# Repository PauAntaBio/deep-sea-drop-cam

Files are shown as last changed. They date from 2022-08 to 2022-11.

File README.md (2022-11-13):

# deep-sea-drop-cam
Blue Eye: a low cost Arduino-powered device to explore the deep sea up to 500 meters of depth at a cost of US$1,400.



In 2018, I attended All Hands on Deck, an event co-organized by the MIT Media Lab and NOAA Office of Ocean Exploration and Research, in which policy makers, scientists, activists and change makers in ocean exploration met to imagine new ways to empower an open, inclusive global community of ocean explorers.

This event motivated me to develop a low cost device to explore the deep sea, after I learned that "70 percent of countries have deep-sea environments within their maritime Exclusive Economic Zones (EEZs), yet only 16 percent of them are able to explore those environments. The scarcity of technological capability and knowledge leads to a lack of exploration, inappropriate or inadequate management decisions, and unaware populations" (source: MIT Media Lab My Deep Sea, My Backyard).

Acknowledgements

Special thanks to Brennan Phillips PhD, Assistant Professor of Ocean Engineering at the University of Rhode Island, for sharing his knowledge, passion and enthusiasm with me. His advice was key for building the Blue Eye (he knows everything, but if he doesn't know, he knows who does!).

Many thanks to Cristobal Huguet for taking me to test the Blue Eye in the marine reserve and to Maria Cefalí PhD and Juancho Movilla PhD (Research Station "Jaume Ferrer" in Menorca, Spain) for their feedback and recommendations.

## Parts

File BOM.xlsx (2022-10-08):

Bill of Materials (BOM)
Note: some prices from 2019 and some from 2022
Items in green are optional
item | distributor | name | units | $ per unit | item cost | subtotals
POWER |  |  |  |  |  | $47.13
Battery for lights and burn-wire (https://www.amazon.com/gp/product/B07VLR5ZW9/ref=ppx_yo_dt_b_search_asin_title?ie=UTF8&psc=1) | Amazon | 3S Lipo Battery - Energy tech RC Battery 11.1V 30C 3000mAh with Deans-T Plug for RC Car Airplane Helicopter FPV Boat Drone | 1 | $21.99 | $21.99
T-plug connector for battery (https://www.amazon.com/gp/product/B07FSPTPWL/ref=ppx_yo_dt_b_asin_title_o01_s00?ie=UTF8&psc=1) | Amazon | OliYin 3pcs Male Deans T-Plug to Male JST Connector Adapter 3.93inch Heavy Duty 20awg Wire(Pack of 3) | 1 | $8.69 | $8.69
Connector cable (https://www.adafruit.com/product/261) | Adafruit | JST PH 2-Pin Cable - Female Connector 100mm | 2 | $0.75 | $1.50
Battery for motherboard (https://www.adafruit.com/product/328) | Adafruit | Lithium Ion Polymer Battery - 3.7v 2500mAh | 1 | $14.95 | $14.95
CAMERA |  |  |  |  |  | $199.89
GoPro Session Hero 5 (https://www.walmart.com/ip/GoPro-HERO-Session-Waterproof-HD-Action-Camera/49933596?athcpid=49933596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) | GoPro | GoPro HERO Session Waterproof HD Action Camera | 1 | $199.89 | $199.89 |  | cost from 2016
MOTHERBOARD |  |  |  |  |  | $224.46
Microcontroller (https://store.arduino.cc/usa/mkr-wifi-1010) | Arduino | Arduino MKR WiFi 1010 | 1 | $33.90 | $33.90
Memory Shield (https://store.arduino.cc/usa/mkr-mem-shield) | Arduino | ARDUINO MKR MEM SHIELD | 1 | $22.90 | $22.90 |  | optional: needed if you want to have a log
microSD card (https://www.amazon.com/Sandisk-Ultra-Micro-UHS-I-Adapter/dp/B073K14CVB) | Amazon | SanDisk 16GB Ultra microSDHC UHS-I Memory Card with Adapter - 98MB/s, C10, U1, Full HD, A1, Micro SD Card - SDSQUAR-016G-GN6MA | 1 | $5.79 | $5.79 |  | optional: needed if you want to have a log
Relay (https://www.seeedstudio.com/Grove-Relay.html) | Seeed Studio | Grove Relay, operate voltage: 3.3V-5V (SKU 103020005) | 1 | $3.20 | $3.20
PCB breadboard (https://www.adafruit.com/product/589) | Adafruit | Adafruit Perma-Proto Quarter-sized Breadboard PCB x 3 units | 1 | $8.50 | $8.50
External switch (https://bluerobotics.com/store/comm-control-power/switch/switch-10-5a-r1/) | Blue Robotics | Power switch | 1 | $14.00 | $14.00
Magnetic switch (https://www.amazon.com/gp/product/B0009SUF08) | Amazon | Magnetic switch | 1 | $6.48 | $6.48
Half sized breadboard (https://www.adafruit.com/product/64) | Adafruit | Half sized breadboard | 1 | $5.00 | $5.00
Temperature and humidity sensor (https://www.adafruit.com/product/393) | Adafruit | AM2302 (wired DHT22) temperature-humidity sensor | 1 | $15.00 | $15.00 |  | optional: needed if you want to measure temperature and humidity inside the device
Resistors | Adafruit | 220 Ohm resistors (Pack 25) | 1 | $0.75 | $0.75
LEDs (https://www.adafruit.com/product/4203) | Adafruit | Diffused 5mm LED Pack - 5 LEDs each in 5 Colors (Pack 25) | 1 | $2.95 | $2.95
Solid wires (https://www.amazon.com/gp/product/B07TX6BX47/ref=ppx_yo_dt_b_search_asin_title?ie=UTF8&psc=1) | Amazon | Solid Wire-Solid Wire Kit-6 Different Colored 30 Feet spools 22 Gauge Jumper Wire- Hook up Wire Kit | 1 | $14.99 | $14.99
Wire connectors | Amazon | WAGO 221 Lever-Nuts 75pc Wire Connector Assortment Pack with Case | 1 | $42.00 | $42.00
Electronics Tray (4" Series) (https://bluerobotics.com/store/watertight-enclosures/4-series/wte4-etray-r1/?wccp_component_selection%5B1549890504%5D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) | Blue Robotics | Electronics Tray (4" Series) | 1 | $49.00 | $49.00
LIGHTS |  |  |  |  |  | $198.00
Lumen Subsea Light (https://bluerobotics.com/store/thrusters/lights/lumen-r2-rp/) | Blue Robotics | Lumen Subsea Light 1500 lumens | 2 | $99.00 | $198.00
HOUSING |  |  |  |  |  | $352.00
Dome end cap (https://bluerobotics.com/store/watertight-enclosures/locking-series/wte-end-cap-vp/) | Blue Robotics | Dome end cap | 1 | $39.00 | $39.00
Flat end cap (https://bluerobotics.com/store/watertight-enclosures/locking-series/wte-end-cap-vp/) | Blue Robotics | Aluminium end cap with 5 holes | 1 | $20.00 | $20.00
Enclosure clamp (https://bluerobotics.com/store/watertight-enclosures/enclosure-clamp/) | Blue Robotics | Enclosure clamp | 1 | $39.00 | $39.00
O-Ring flange (https://bluerobotics.com/store/watertight-enclosures/locking-series/wte-flange-vp/) | Blue Robotics | O-Ring flange | 2 | $29.00 | $58.00
Aluminum tube (https://bluerobotics.com/store/uncategorized/wte4-m-tube-12-r3-rp/) | Blue Robotics | Aluminum tube 11.75" | 1 | $180.00 | $180.00
Pole clamp | Own design | Own design (see 3D parts folder) | 1 | $0.00 | $0.00
Lights mount | Own design | Own design (see 3D parts folder) | 2 | $0.00 | $0.00
Cable penetrator (https://bluerobotics.com/store/cables-connectors/penetrators/penetrator-vp/) | Blue Robotics | Cable penetrator for 6mm cable x 3 | 3 | $4.00 | $12.00
Cable penetrator blank (https://bluerobotics.com/store/cables-connectors/penetrators/penetrator-blank-vp/) | Blue Robotics | Cable penetrator for 6mm blank | 1 | $4.00 | $4.00
DROP AND RELEASE MECHANISM |  |  |  |  |  | $168.34
Carbon fiber tube (https://dragonplate.com/carbon-fiber-roll-wrapped-twill-tube-075-id-x-24-gloss-finish) | All Red | Carbon Tube .75" x .875" x 24" | 1 | $32.54 | $32.54
Top Modular Connector (https://dragonplate.com/075-Male-Clevis-Connector) | All Red | Modular Connector .75" Male Clevis Connector | 1 | $11.00 | $11.00
Bottom Modular Connector (https://dragonplate.com/075-short-threaded-end-connector) | All Red | Modular Connector .75" Short Threaded End Conn. (1/4-20) | 1 | $10.50 | $10.50
Link bottom Modular Connector (https://dragonplate.com/link-for-075-modular-connectors-3-hole) | All Red | Modular Connector .75" 3 Hole Link | 1 | $7.00 | $7.00
Epoxy adhesive (https://dragonplate.com/Double_Bubble-Orange-High-Peel-Strength-Epoxy-Adhesive) | All Red | Double/Bubble Orange High Peel Strength Epoxy Adhesive | 1 | $1.40 | $1.40
Bolts (https://dragonplate.com/Stainless-Steel-Black-Oxide-Bolt--075-x-1_4-20-thread) | All Red | Black Oxide SS 1/4-20x3/4 BHCS Black Oxide | 4 | $0.35 | $1.40
Ring terminals (https://www.mcmaster.com/catalog/125/817) | McMaster-Carr | Heat-Shrink Ring Terminals for 22-18 Wire Gauge and 1/4" Screw Size (pack of 10) | 1 | $7.54 | $7.54
loop to loop lanyard (https://www.mcmaster.com/catalog/125/1524) | McMaster-Carr | 18-8 Stainless Steel Lanyard - Not for Lifting, Loop-to-Loop, 1/16" Rope Diameter, 6" Long, Nylon | 1 | $2.80 | $2.80
Burnwire (https://www.amazon.com/gp/product/B07CHTY1VV/ref=ppx_yo_dt_b_asin_title_o02_s01?ie=UTF8&psc=1) | Amazon | Fast Fog 50 ft - 30 Gauge AWG Nichrome 80 Resistance Wire 50’ Length | 1 | $7.81 | $7.81
Biodegradable bags (https://www.amazon.com/gp/product/B07P6NN4RV/ref=ppx_yo_dt_b_asin_title_o02_s00?ie=UTF8&psc=1) | Amazon | 100% Organic Cotton, Biodegradable and Reusable Premium Quality Muslin Drawstring Bags,Size : 10x12 inches (Pack of 25) | 1 | $31.99 | $31.99
Biodegradable cord (https://www.amazon.com/Macrame-Cord-109Yards（328Feet-Natural-Cotton/dp/B09CNT9RZC) | Amazon | 3mm x 109Yards (328Feet), Natural Cotton Macrame Rope | 1 | $9.99 | $9.99
Nylon 3mm outdoor cord (https://www.amazon.com/TRIWONDER-Reflective-Paracord-Guyline-Packaging/dp/B07FKHDGC9) | Amazon | Reflective Nylon Paracord, Tent Guyline Rope for Camping Tent, Outdoor Packaging, 50 Feet Cord | 1 | $6.99 | $6.99
Weigth (https://www.amazon.com/Scuba-Choice-Coated-Diving-Weights/dp/B01M1RJ976) | Amazon | Scuba Choice Blue Vinyl Coated Diving Lead Weights, 2LB | 1 | $14.18 | $14.18
Deep water float |  | See picture in GitHub repository | 1 | $5.00 | $5.00
Galvanic release (https://www.lfsmarineoutdoor.com/Neptune-Galvanic-Time-Release?quantity=1&type=632) | LFS Marine outdoor | Neptune Galvanic Time Release 1 day | 10 | $1.82 | $18.20
ADDITIONAL COMPONENTS |  |  |  |  |  | $220.15
Vent plug (https://bluerobotics.com/store/cables-connectors/penetrators/vent-m-plug-10-a-r1/) | Blue Robotics | Vent plug | 1 | $4.00 | $4.00
Vacuum plug (https://bluerobotics.com/store/watertight-enclosures/enclosure-tools-supplies/vacuum-plug/) | Blue Robotics | Vacuum plug | 1 | $8.00 | $8.00
Vacuum pump (https://www.amazon.com/gp/product/B00KB9D3UO/ref=ppx_yo_dt_b_asin_title_o05_s00?ie=UTF8&psc=1) | Amazon | ABN Brake Bleeder Kit Universal Vacuum Pump & Brake Bleeding Tester Set for Automotive Service & Airtight Food Canning | 1 | $20.99 | $20.99
Silicone (https://bluerobotics.com/store/watertight-enclosures/enclosure-tools-supplies/tool-silicone-grease-10g-r1/) | Blue Robotics | Silicone grease 10g | 1 | $3.00 | $3.00
Potting kit (https://bluerobotics.com/store/cables-connectors/tools/tool-potting-kit-r1/) | Blue Robotics | Potting kit | 1 | $10.00 | $10.00
Acetone wipes (https://bluerobotics.com/store/cables-connectors/tools/potting-acetone-wipes-qty10-r1-rp/) | Blue Robotics | Acetone cable preparation wipes (10 pcs) | 1 | $4.00 | $4.00
Potting compound (https://bluerobotics.com/store/cables-connectors/tools/potting-thx-80a-r1/) | Blue Robotics | WetLink Thixotropic 80A Potting Compound (USA ONLY) | 1 | $19.00 | $19.00
Potting dispenser (https://bluerobotics.com/store/cables-connectors/tools/potting-dispenser-r1-rp/) | Blue Robotics | Potting cartridge dispenser | 1 | $23.00 | $23.00
Cable zip ties (https://www.amazon.com/HAVE-ME-TD-Cable-Ties/dp/B08TVLYB3Q) | Amazon | Cable Zip Ties,400 Pack Black Zip Ties Assorted Sizes 12+8+6+4 Inch | 1 | $6.59 | $6.59
Bait bag (https://www.lfsmarineoutdoor.com/Flexible-Bait-Bag-Material) | LFS Marine outdoor | Flexible Bait Bag Material | 1 | $0.25 | $0.25
Stainless Steel Screws and Nuts (https://www.amazon.com/gp/product/B071KBVZVV/ref=ppx_yo_dt_b_asin_title_o06_s00?ie=UTF8&psc=1) | Amazon | VIGRUE M2-M3-M4-1080PCS Stainless Steel Screws and Nuts, 1080 Pcs Hex Socket Head Cap, Silver | 1 | $25.99 | $25.99
Lipo battery storage (https://www.amazon.com/gp/product/B005HTH78W/ref=ppx_yo_dt_b_asin_title_o02_s00?ie=UTF8&psc=1) | Amazon | Aketek Silver Large Size Lipo Battery Guard Sleeve/Bag for Charge & Storage | 1 | $7.77 | $7.77
Velcro (https://www.amazon.com/VELCRO-Brand-Sticky-Fasteners-Perfect/dp/B00006IC2M?__mk_es_US=ÅMÅŽÕÑ) | Amazon | VELCRO Brand 5 Ft x 3/4 In | White Tape Roll with Adhesive | 1 | $8.00 | $8.00
Electric tape (https://www.amazon.com/Scotch-Heat-Resistant-Listed-Certified-Electrical/dp/B001AXD0EY) | Amazon | Scotch Vinyl Electrical Tape, Black, 3/4-in by 66-ft, 1-Roll | 1 | $2.06 | $2.06
VHB tape (https://www.amazon.com/Double-Mounting-Waterproof-Outdoor-Black，1/dp/B08T1HB5LJ) | Amazon | Double Sided Tape, 3M Heavy Duty Mounting Tape, Waterproof VHB Foam Tape | 1 | $9.00 | $9.00
USB for Arduino (https://www.amazon.com/AmazonBasics-Male-Micro-Cable-Black/dp/B0711PVX6Z?hvadid=198093101467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) | Amazon | AmazonBasics USB 2.0 A-Male to Micro B Charger Cable, 3 feet | 1 | $4.99 | $4.99
Battery charger (3S lipo) (https://www.amazon.com/Charger-Balance-Discharger-Digital-Batteries/dp/B07V5CPYRS) | Amazon | LiPo Charger RC Balance Fast Charger Discharger 1S-6S AC/DC B6V2 Digital Battery Pack Charger for NiCd Li-ion Life NiMH LiHV PB Smart Batteries | 1 | $46.57 | $46.57
Battery charger (micro-lipo) (https://www.adafruit.com/product/1904) | Adafruit | Adafruit Micro-Lipo Charger for LiPo/LiIon Batt w/MicroUSB Jack - v1 P | 1 | $6.95 | $6.95
Power supply cord (https://www.amazon.com/Pinfox-Universal-Appliance-Replacement-Pigtail/dp/B06XRKXLVV?s=hi) | Amazon | Pinfox 6ft 16 Gauge 3 Prong Heavy Duty Replacement Power Supply Cord Cable 110V 115V 120V Pigtail for Universal AC Appliance, NEMA 5-15 Plug US SJT 16AWG (12A) | 1 | $9.99 | $9.99
 |  |  |  | Total cost | $1409.97
TOOLS
Terminal Crimper Tool (https://www.amazon.com/gp/product/B0069TRKJ0/ref=ppx_yo_dt_b_asin_title_o03_s00?ie=UTF8&psc=1) | Amazon | Titan Tools 11477 Ratcheting Wire Terminal Crimper Tool | 1 | $18.95 | $18.95
Solder (https://www.amazon.com/ANBES-Soldering-Iron-Kit-Electronics/dp/B06XZ31W3M) | Amazon | ANBES Soldering Iron Kit Electronics, 60W Adjustable Temperature Welding Tool | 1 | $17.99 | $17.99
Solder wire (https://www.amazon.com/gp/product/B00AYJ0B7Y/ref=ppx_yo_dt_b_asin_title_o05_s00?ie=UTF8&psc=1) | Amazon | Kester 44 Rosin Core Solder 63/37 .020" 3/4oz Dispense-Pak | 1 | $11.89 | $11.89
Soldering tip (https://www.amazon.com/gp/product/B00762AGTA/ref=ppx_yo_dt_b_asin_title_o05_s00?ie=UTF8&psc=1) | Amazon | Hakko T18BL Series Soldering Tip for FX-888/FX-8801, Conical, R 0.2 mm x 22.5 mm | 1 | $9.46 | $9.46
Clip test leads (https://www.adafruit.com/product/1008) | Adafruit | Small Alligator Clip Test Lead (set of 12) | 1 | $3.95 | $3.95
Digital multimeter (https://www.amazon.com/Etekcity-Multimeter-MSR-R500-Electronic-Multimeters/dp/B01N9QW620) | Amazon | Etekcity Digital Multimeter, Amp Volt Ohm Voltage Tester Meter with Diode and Continuity Test, Dual Fused for Anti-Burn | 1 | $9.15 | $9.15
Wire strippers (https://www.amazon.com/VISE-GRIP-Stripping-Cutter-8-Inch-2078309/dp/B000JNNWQ2) | Amazon | IRWIN Vise-Grip Wire Stripping Tool / Wire Cutter, 8-Inch (2078309) | 1 | $14.00 | $14.00
Hex key set (https://www.amazon.com/30-Piece-Premium-Assortment-Vanadium-Chamfered/dp/B08GKHLJWR) | Amazon | Hex Key Allen Wrench Set | 1 | $12.99 | $12.99
Clamp on vise (https://www.amazon.com/MYTEC-Home-Vise-Clamp-3-0/dp/B07T5RL3DM) | Amazon | Clamp on vise | 1 | $27.87 | $27.87
Helping hands (https://www.amazon.com/Third-Soldering-Workshop-Non-Slip-Aluminum/dp/B079CHJQKH) | Amazon | Adjustable helping hands for soldering | 1 | $29.99 | $29.99

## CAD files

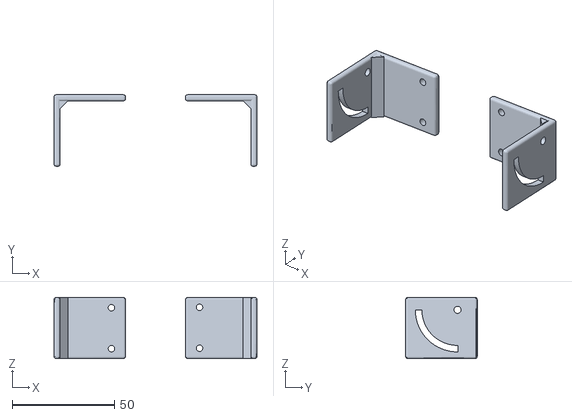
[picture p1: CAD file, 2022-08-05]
3D parts/light support.stl
99.3 x 35.0 x 30.0

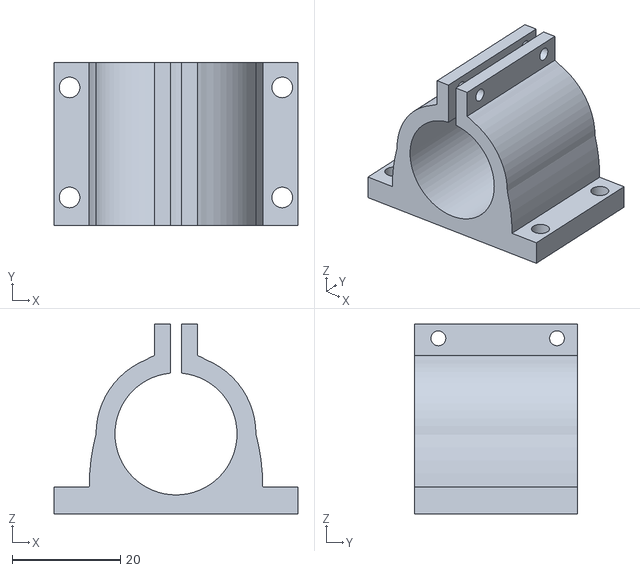
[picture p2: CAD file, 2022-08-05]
3D parts/pole clamp.stl
45.0 x 30.0 x 35.0

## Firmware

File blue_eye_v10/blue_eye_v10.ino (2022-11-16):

// Project Blue Eye
// by Pau Anta, more information at http://www.pauanta.bio
// This code has an MIT License

// Development of an open-source low-cost deep-sea drop-cam for marine exploration
// Inspired in the Drop-Cam invented by Alan Turchik, National Geographic Innovation Labs
// Advised by Brennan Phillips, Rhode Island University, https://web.uri.edu/oce/brennan-phillips/

// Started development on December 2018
// Goal: up to 500m of depth, for a maximum cost of $500. However, the Bill of Materials to build this model costs about $1,400
// The Blue Eye is a device controlled by an Artuino MKR WiFi, connected to a GoPro Hero5 Session

// Code to connect Arduino to GoPro's wifi and control its video features written by @randofo from Instructables, license CC BY-NC-SA 4.0

// January 2019 - system is activated by a contactless magnetic switch
// April 2019 - from v6, code introduces millis() instead of delay() to allow for running code while waiting (dropTime and recordingTime).
// April 2019 - integrated temp and humidity sensor
// May 2019 - integrated lightning control
// June 2019 - burnwire coded
// July 2019 - tests in the marine biosphere reserve in Menorca at 50 meters deep
// October 2019 - refinement of features and added tech specs in comments
// May 2022 - refinement of burnwire, added PWM to lights
// Aug 2022 - tests in Menorca.
// October 2022 - release of design, assembly guide, 3D parts and code in GitHub.

// Gopro Hero 5 session
// Key aspects of GoPro's statuses
// - Time it takes to Arduino to connect to GoPro: between 6 and 8 seconds
// - MAX time between turning GoPro ON and turning electronic switch of the blue eye ON: 2 minutes
// - MAX time between connection of Arduino to GoPro and wake up GoPro: 3 minutes
// - MAX time between stop recording and connecttoGoPro again: 2 minutes 
// - MAX time GoPro is awake before it sleeps down: 5 minutes

// T0 - turn GoPro on
// T1 - turn electronic switch (ES) on. T1 = T0 + max 2 minutes
// T2 - Arduino connects to GoPro. T2 = T1 + 6 seconds aprox.
// T3 - turn magnetic switch (MS) on: loop program starts and wakes up GoPro. T3 = T2 + max 3 minutes
//      droptime max 5 minutes
// T4 - GoPro starts recording. T4 = T3 + droptime


#include <RTCZero.h>
#include <SD.h>
#include <SPI.h>
#include <WiFiNINA.h>
#include <WiFiUdp.h>
#include "wifi.h"
#include "DHT.h"

const int oneMinute = 60000;      // 60,000 millisecons = 1 minute
                                  // settings for the mission
int dropTime = 1;                 // estimated duration to get to the seabed in minutes
                                  // it CAN'T be more than 5m. GoPro turns into sleep mode after 5m
int recordingTime = 20;           // duration of video recording in minutes

unsigned long time_now = 0;
                                  // LEDs for signaling status
const int LEDstatus = 0;          // OUT BLUE signals the blue_eye is on (it has power)
const int LEDmagswitch = 1;       // OUT YELLOW signals the magnetic switch has been activated
const int LEDwifi = 2;            // OUT GREEN signals Arduino is connected to GoPro's WiFi.
const int DHTPin = 3;             // IN read values of humidity and temperature sensor
const int chipSelect = 4;         // selection of SD card in Arduino MKR MEM shield
const int lightsPin = 5;          // OUT turn lights on/off
const int magswitchPin = 6;       // IN read magnetic switch (MS)
const int burnwirePin = 7;        // OUT activates burnwire
bool justWait = true;             // variable to prevent repetition of loop 

int switchState;                  // status of magnetic switch
#define DHTTYPE DHT22             // AM2303 is a wired DHT22 sensor for temp and humidity             
DHT dht(DHTPin, DHTTYPE);         // Initialize DHT sensor
                                  
char ssid[] = SECRET_SSID;        // Wifi's SSID of GoPro, in wifi.h
char pass[] = SECRET_PASS;        // Wifi's password of GoPro, in wifi.h
int status = WL_IDLE_STATUS;
int localPort = 7;
byte broadCastIp[] = { 10,5,5,9 };
byte remote_MAC_ADD[] = { 0xf6, 0xdd, 0x9e, 0x82, 0x7d, 0x4e };
int wolPort = 9;
const char* host = "10.5.5.9";
const int httpPort = 80;

#define nameLog "log.txt"         // File name of Log

WiFiUDP Udp;
WiFiClient client;

// variables for timer
const byte seconds = 0;
const byte minutes = 0;
const byte hours = 0;

RTCZero rtc;

// SET UP of the program
void setup() {

  // WARNING - Serial communications only activated when testing and debuggind with serial monitor.
  // Serial.begin(9600);
  // while (!Serial) {
  //  }

  // setup pins
  pinMode (magswitchPin, INPUT_PULLUP);
  pinMode (lightsPin, OUTPUT);
  pinMode (burnwirePin, OUTPUT);  
  
  digitalWrite (burnwirePin, LOW);

  pinMode (LEDstatus, OUTPUT);
  pinMode (LEDmagswitch, OUTPUT);
  pinMode (LEDwifi, OUTPUT);

  // turns on LED blue: blue_eye is ON
  digitalWrite (LEDstatus, HIGH);

  printInLog("Hello! Welcome to the blue_eye 2.0");

  // initialize and set up timer
  rtc.begin();
  rtc.setHours(hours);
  rtc.setMinutes(minutes);
  rtc.setSeconds(seconds);

  dht.begin();

  // check if SD card is present and can be initialized:
  if (!SD.begin(chipSelect)) {
    printInLog("SD card failed, or not present in MEM Shield");
    while (1);
  }
  else{
    initializeLog();
  }

  // check for the presence of the wifi in Arduino
  if (WiFi.status() == WL_NO_SHIELD) {
      printInLog("WiFi chipset not present in Arduino");
     while (true);
  }

  ConnectToGoPro();

}


void loop() {

  MagneticSwitch();         // user turns MS only when is ready to drop the blue eye. MAX time between ES and MS is 3m. After that, GoPro sleeps down

  WakeupGoPro();
  
  time_now = millis();
  
  printInLog("blue_eye on its way to the deep sea");

  while(millis() < time_now + (dropTime * oneMinute)){
     readDHT22Values();
     delay(oneMinute);
  }

  printInLog("blue_eye arrived to the seabed");

  printInLog("Turning lights on");

  // turns on lights gradually 
  for(int i=0; i<255; i++){
    analogWrite(lightsPin, i);
    delay(5);
  }

  StartRecording();         // it may be nice to start recording soon after you drop the camera so you can record how light change as the camera goes down 

  time_now = millis();

  // during recording time, checks humidity and temperature every minute
  while(millis() < time_now + (recordingTime * oneMinute)){
    readDHT22Values();
    delay(oneMinute);
  }

  // if you want to play with lights intensity, on or off, this is the place to do it 

  StopRecording();
  
  // turns off lights gradually 
  for(int i=255; i>0; i--){
    analogWrite(lightsPin, i);
    delay(50);
  }

  digitalWrite(lightsPin, LOW);
 
  printInLog("Turning lights off");

  BurnWire();

  DisconnectFromGoPro();

  digitalWrite (LEDmagswitch, LOW);

  while(justWait == true) {
  }

}

// Arduino attempts to connect to GoPro's wifi network, developed by @randofo from Instructables

void ConnectToGoPro(){
  
  status = WiFi.begin(ssid, pass);

  while ( status != WL_CONNECTED) {
    printInLog("Arduino is attempting to connect to GoPro's WiFi ...");
    printInLog(String(status));
    for (int i = 0; i <= 1; i++){
      digitalWrite(LEDwifi, HIGH);    // blinking LED green
      delay(1000);
      digitalWrite(LEDwifi, LOW);
      delay(1000);
    }
  }

  printInLog("Arduino is connected to GoPro's WiFi network");
  
  digitalWrite (LEDwifi, HIGH);       // LED green turns on after GoPro is connected

  for (int i = 0; i <= 2; i++) {      // lights blink three times after Arduino connects to gopro
     digitalWrite(lightsPin, HIGH);
     delay(500);
     digitalWrite(lightsPin, LOW);
     delay(500);
  }
  
  // printWifiStatus();

}


// Arduino disconnects from GoPro's WiFi, developed by @randofo from Instructables
void DisconnectFromGoPro(){

  WiFi.disconnect();

  digitalWrite (LEDwifi, LOW);

}


//controls activation with magnetic switch 
void MagneticSwitch(){

  digitalWrite(LEDmagswitch, LOW);

  switchState = digitalRead(magswitchPin);
  
  while (switchState == HIGH){
     switchState = digitalRead(magswitchPin);
   }

  digitalWrite(LEDmagswitch, HIGH);

  printInLog("Magnetic switch activated");
  
}


// wake up GoPro, developed by @randofo from Instructables
void WakeupGoPro(){

  //Begin UDP communication
  Udp.begin(localPort);

  //Send the magic packet to wake up the GoPro out of sleep
  delay(2000);
  SendMagicPacket();
  delay(6000);  

  // Absolutely necessary to flush port of UDP junk for Wifi client communication
  Udp.flush();
  delay(1000);

  //Stop UDP communication
  Udp.stop();
  delay(1000);

  printInLog("Waking up GoPro");
  
}


// Function to create and send magic packet, developed by @randofo from Instructables
// https://www.logicaprogrammabile.it/wol-accendere-computer-arduino-wake-on-lan/

void SendMagicPacket(){

  //Create a 102 byte array
  byte magicPacket[102];

  // Variables for cycling through the array
  int Cycle = 0, CycleMacAdd = 0, IndexArray = 0;

  // This for loop cycles through the array
  for( Cycle = 0; Cycle < 6; Cycle++){

    // The first 6 bytes of the array are set to the value 0xFF
    magicPacket[IndexArray] = 0xFF;

    // Increment the array index
    IndexArray++;
  }

  // Now we cycle through the array to add the GoPro address
  for( Cycle = 0; Cycle < 16; Cycle++ ){

    //eseguo un Cycle per memorizzare i 6 byte del mac address
    for( CycleMacAdd = 0; CycleMacAdd < 6; CycleMacAdd++){
      
      magicPacket[IndexArray] = remote_MAC_ADD[CycleMacAdd];
      
      // Increment the array index
      IndexArray++;
    }
  }

  //The magic packet is now broadcast to the GoPro IP address and port
  Udp.beginPacket(broadCastIp, wolPort);
  Udp.write(magicPacket, sizeof magicPacket);
  Udp.endPacket();

}


void StartRecording(){
  
  if (!client.connect("10.5.5.9", httpPort)) {
    printInLog("Start recording failed");
    return;
  }

  //Command for start recording
  String StartUrl = "/gp/gpControl/command/shutter?p=1";
  client.print(String("GET ") + StartUrl + " HTTP/1.1\r\n" +
  "Host: " + host + "\r\n" +
  "Connection: close\r\n\r\n");

  printInLog("GoPro started recording");
  
}


void StopRecording(){
  
  if (!client.connect("10.5.5.9", httpPort)) {
    printInLog("Stop recording failed");
    return;
  }

  //Command for stopping recording, developed by @randofo from Instructables
  
  String StopUrl = "/gp/gpControl/command/shutter?p=0";
  client.print(String("GET ") + StopUrl + " HTTP/1.1\r\n" +
  "Host: " + host + "\r\n" +
  "Connection: close\r\n\r\n");

  printInLog("GoPro stopped recording");

}


void initializeLog(){

  if (SD.exists(nameLog)) {     // removes previous file in order to start a new log
    SD.remove(nameLog);       
  }

}


// coding for logging in a text file stored in microSD card 
void printInLog(String dataString){

  File dataFile = SD.open(nameLog, FILE_WRITE);

  if (dataFile) {
    dataFile.println(String(rtc.getHours()) 
    + ":" + String(rtc.getMinutes()) 
    + ":" + String(rtc.getSeconds()) 
    + "\t" + dataString);
    dataFile.close();

    // WARNING :: need to comment this part for real deployment

    // Serial.println(String(rtc.getHours()) 
    //  + ":" + String(rtc.getMinutes()) 
    //  + ":" + String(rtc.getSeconds()) 
    //  + "\t" + dataString);
    
  }
  else {
//    Serial.println("Error opening log");
  }
}


void printWifiStatus() {

  // print your WiFi shield's IP address:
  IPAddress ip = WiFi.localIP();
  printInLog("IP Address: " + String(ip));

  // print the received signal strength:
  long rssi = WiFi.RSSI();
  printInLog("signal strength:" + String(rssi) + "dBm");

}
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
